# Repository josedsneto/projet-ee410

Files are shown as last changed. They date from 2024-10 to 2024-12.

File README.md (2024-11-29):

# Détecteur de chute

Nous souhaitons développer un capteur de chute, à l'aide d'un axéléromètre 3 Axes.
Lorsqu'une chute est détectée : 
- Une alerte via un vibreur est transmise à l'utilisateur.
- Il dispose de 10 secondes pour confirmer qu'il ne s'est pas évanoui via un bouton.
- Si il a confirmé qu'il était conscient, rien ne se passe.
- En revanche, si il n'a rien confirmé alors une alerte est envoyé par bluetooth sur le téléphone.

## Planning et Deadlines

- 04 Octobre 2024 : Choix du système visé (Remettre une page décrivant le système
imaginé, les mesures qui seront faites + toute autre info pertinente) \
Le [lien](https://docs.google.com/document/d/1k7mpjtoi8ii_IY9sKmL_kZ1YLawBmLwHGLVDXy7D6bw/edit?usp=sharing) vers le document
- 17 Octobre 2024 : Commande de composants 
- 24 Octobre 2024 : Evaluation intermédiaire
- 29 Novembre 2024 : Présentation orale
- 06 Décembre 2023 : Rendu du rapport final écrit 

## Critères pour les profs

L'idée est de faire une première application avec un module compatible Arduino. 
Puis de faire une autre version où on part du composant seul (ou package) et de faire un PCB autour du composant.

A la fin, il faudra comparer les deux.\
Dans notre cas, il s'agit d'un tout ou rien : détection ou non détection. \
Mais nous pouvons récupérer les valeurs des accélérations des 2 capteurs et comparer leurs valeurs.\
De plus nous pouvons réaliser un test statistique sur la détection de chute. (exemple en dessous)

| Cas réel -> | Statique | Chute | Marche |
|-------------|:--------:|:-----:|:------:|
| Statique    |   99%    |  1%   |   0%   |
| Chute       |   1.5%   |  98%  |  0.5%  |
| Marche      |    5%    |  25%  |  70%   |

Et aussi pour la comparaison des 2 capteurs

|                | Capteur1 | Capteur2 |
|----------------|:--------:|:--------:|
| Statique       |   99%    |   99%    |
| Marche         |   97%    |   98%    |
| Chute droite   |   80%    |   98%    |
| Chute en avant |   95%    |   95%    |

Et ainsi comparer nos 2 capteurs.\
Certes nous n'avons que des valeurs tout ou rien mais nous pouvons dire par plusieurs paramètres si un capteur est mieux qu'un autre.

### Réalisation de tests

Il va falloir pouvoir réaliser des tests qui sont reproductibles !\
Il faut pouvoir obtenir le même résultat en faisant une même manip plusieurs fois.

- Test de la chute droite : 
    - Récupération des valeurs lorsqu'un humain chute, pour avoir une idée de modèle.
    - On peut modéliser cette chute avec un ballon qui tombe sur un matelas en mousse par exemple. Ceci permettra une certaine reproductibilité.
- Test de la chute en avant : 
    - Pareil, récupération des valeurs pour un humain
    - Modélisation par exemple par un balai qui tombe en avant.

**Notes sur les chutes :**
- Faire attention à l'orientation du capteur, son positionnement sur le témoin
- Pouvoir reproduire la chute en toutes conditions

# Capteur de chute V1

On utilise le code ```CapteurChuteV1.ino```

Lorsqu'une chute se passe voici ce que nous pouvons mesurer : 

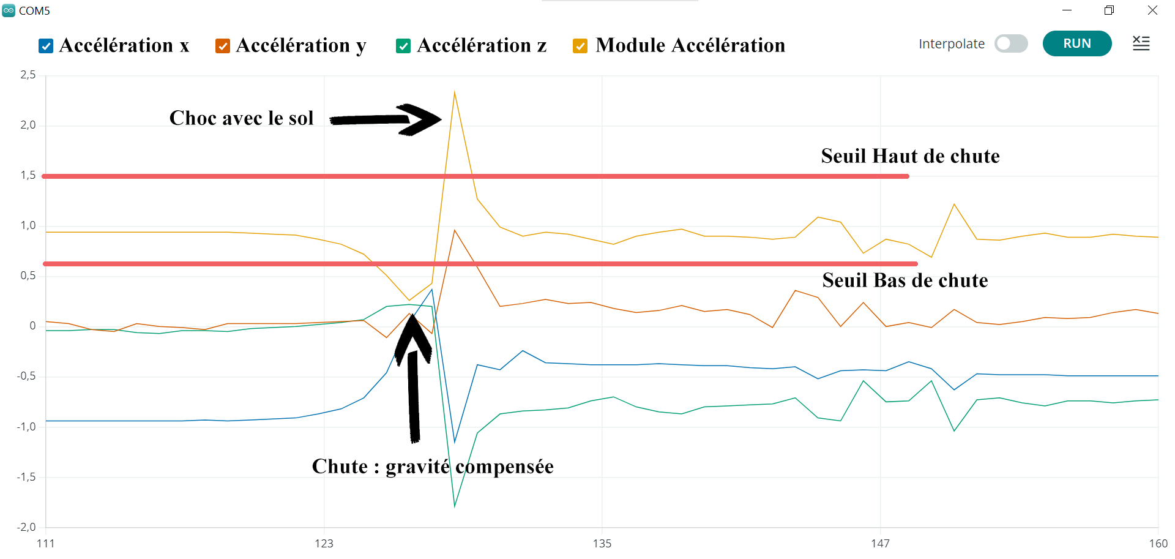
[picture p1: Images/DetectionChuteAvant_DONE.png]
Schéma temporel de la détection de chute


Lorsque le module passe en dessous du seuil bas, c'est le début de la chute : la gravité est compensée par la chute.\
Puis on repasse au dessus du seuil haut, c'est lorsqu'on heurte le sol : gravité + impact avec le sol.

Badé sur ce modèle, nous créons le code arduino ```CapteurChuteV1.ino```, qui utilise un diagramme d'état. \
Voici son schéma : 

Diagramme Etat V1

# Le nouveau capteur

Nous rédigeons un tableau comparatif entre les 2 capteurs : 

|                      |      ADXL 345       |      ADXL 359      |
|----------------------|:-------------------:|:------------------:|
| Interface            |      SPI, I²C       |      SPI, I²C      |
| Technologie utilisée |        MEMS         |        MEMS        |
| Plage de mesure      | ±2g, ±4g, ±8g, ±16g |  ±10g, ±20g, ±40g  |
| Résolution           |       13 bits       |      20 bits       |
| Bruit                |     380 µg/√Hz      |     80 µg/√Hz      |
| 0g Offset            |        ±150 mg      |       ±125 mg      |
| Taille du boîtier    | 3 mm × 5 mm × 1 mm  | 4 mm × 4 mm × 1 mm |

**La technologie MEMS (Micro-Electro-Mechanical Systems).**\
 Un dispositif MEMS est composé de minuscules éléments comme des ressorts, des leviers et des masses mobiles  qui sont gravés sur du silicium.\
 Lorsqu'une force externe (comme une accélération) agit sur ces éléments, cela provoque un mouvement des masses et viens déformer les ressorts. Ce mouvement viens changer la valeur de capacité, ce qui vient influer sur le signal électrique, nous récupérons ainsi des informations sur l'accélération.

Voici le schéma de l'ADXL 359.

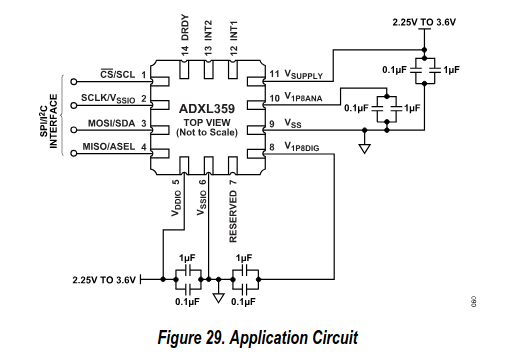
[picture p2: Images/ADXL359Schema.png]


| Pin N° | Mnemonic |                                                                                            Description                                                                                            |
|--------|:--------:|:-------------------------------------------------------------------------------------------------------------------------------------------------------------------------------------------------:|
| 1      |   SCL    |                                                                             Serial Communications Clock for I2C (SCL)                                                                             |
| 2      |  Vssio   |                                                                           Connected to Pin 6 (VSSIO) to enable I2C mode                                                                           |
| 3      |   SDA    |                                                                                    Serial Data for I2C (SDA).                                                                                     |
| 4      |   ASEL   |                                                                           Alternate I2C Address Select for I2C (ASEL).                                                                            |
| 5      |  Vddio   |                                                                                 Digital Interface Supply Voltage                                                                                  |
| 6      |  Vssio   |                                                                                          Digital Ground                                                                                           |
| 7      | RESERVED |                                                                    Reserved. This pin can be connected to ground or left open.                                                                    |
| 8      | V1P8DIG  |                                 Digital Supply. This pin requires a decoupling capacitor. If VSUPPLY connects to VSS, supply the voltage to this pin externally.                                  |
| 9      |   Vss    |                                                                                           Analog Ground                                                                                           |
| 10     | V1P8ANA  |                                  Analog Supply. This pin requires a decoupling capacitor. If VSUPPLY connects to VSS, supply the voltage to this pin externally.                                  |
| 11     | VSUPPLY  | Supply Voltage. When VSUPPLY equals 2.25 V to 3.6 V, VSUPPLY enables the internal LDO regulators to generate V1P8DIG and V1P8ANA. For VSUPPLY = VSS, V1P8DIG and V1P8ANA are externally supplied. |
| 12     |   INT1   |                                                                                          Interrupt Pin 1                                                                                          |
| 13     |   INT2   |                                                                                          Interrupt Pin 2                                                                                          |
| 14     |   DRDY   |                                                                                          Data Ready Pin.                                                                                          |

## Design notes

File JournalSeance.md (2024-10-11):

# Séance 1 : 13 Septembre 2024

Découverte du projet. \
Lecture des attendus.\
Légère prise en main de la boite Arduino.

## Séance 2 : 20 Septembre 2024

Prise en main des capteurs de la boite.\
Tutoriel sur les capteurs suivants : 
- Capteur d'humidité
- Bouton
- Module Bluetooth
- 7 Segement Display

## Séance 3 : 27 Septembre 2024

Création du ```README.md```, définition des tests.\
Echange avec le prof sur le sujet.\
Renseignement sur manière de caractériser notre capteur.\
Prise en main de capteur, communication Bluetooth, test du buzzer avec l'accéléromètre.

## Séance 4 : 4 Octobre 2024

- [X] Exporter des donnés au format csv (du capteur)
- [ ] Chercher capteur équivalent (non Arduino) et se renseigner sur la circuiterie autour
- [ ] Création du fichier de rapport
- [X] Faire le fichier sur l'application Technique

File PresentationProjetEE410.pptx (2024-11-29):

## Capteur de Chute

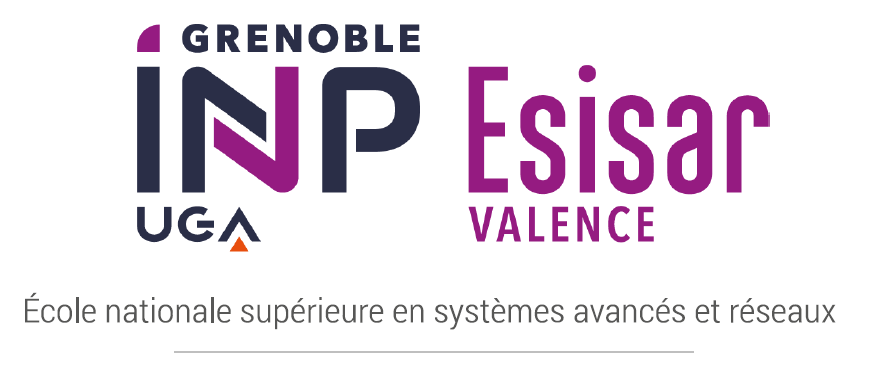
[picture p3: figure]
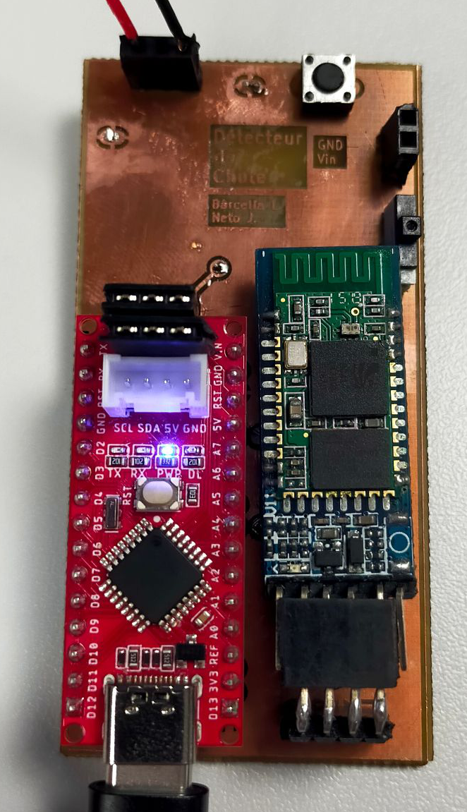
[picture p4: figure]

Projet EE410, Année 2024-2025
Léo BARCELLA & José NETO

## Fonctionnement du capteur (1/2)

Principe général : Fonctionnement simplifié

Technologie MEMS (Micro Systèmes Electromécaniques) :
- Une petite “masse suspendue” bouge sous l’effet de l’accélération
- Capteurs capacitifs mesurent le déplacement
- Mesures transformées en données d’accélération

## Fonctionnement du capteur (2/2)

Illustration du principe

Technologie MEMS (Micro Systèmes Electromécaniques) :

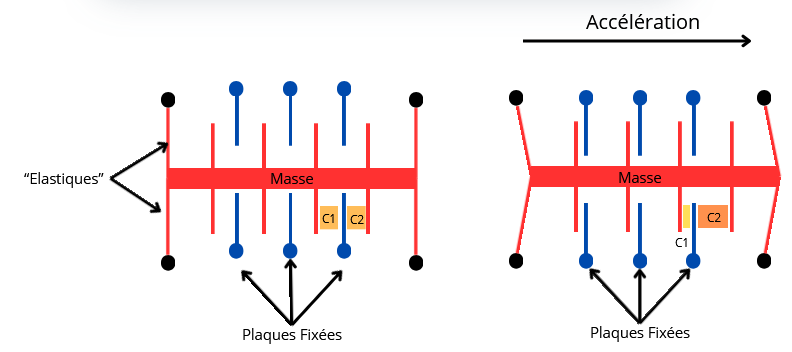
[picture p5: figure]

## Application du capteur (1/3)

Simulation d’un chute

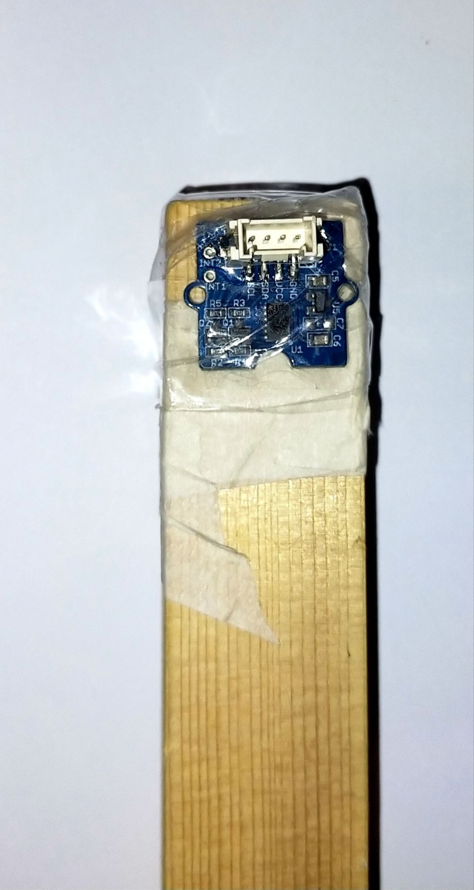
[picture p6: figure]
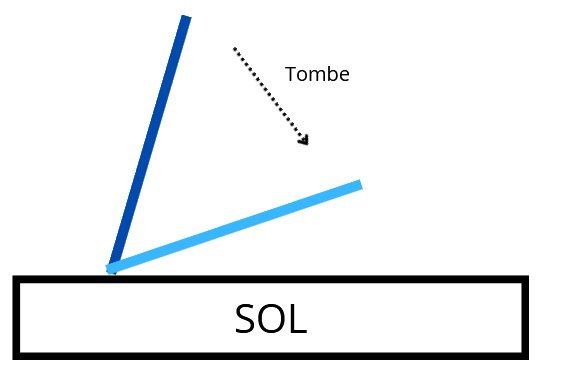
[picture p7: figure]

ADXL345

## Application du capteur (2/3)

Principe général

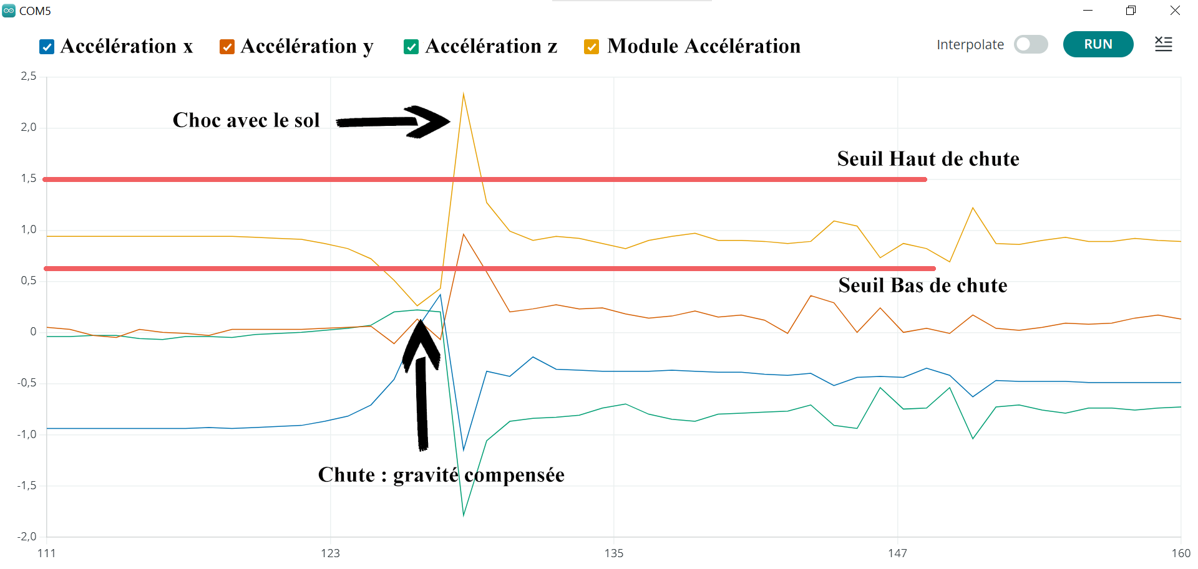
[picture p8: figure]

## Application du capteur (3/3)

Calcul des seuils

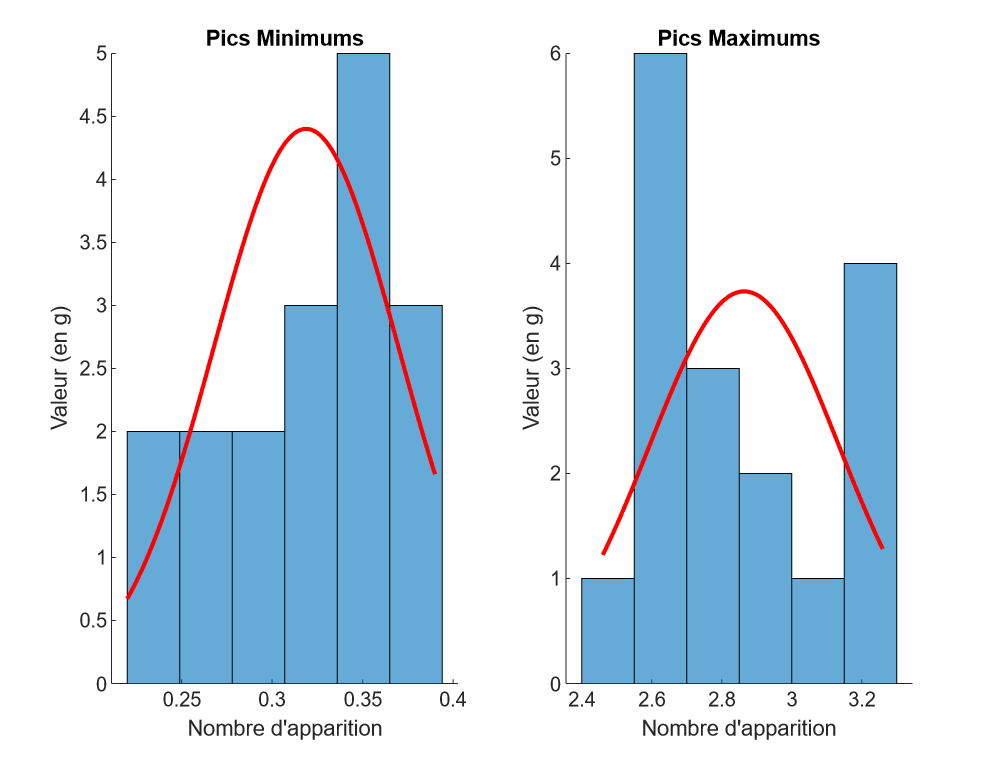
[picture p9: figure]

## Présentation rapide du code

Machine de Mealy

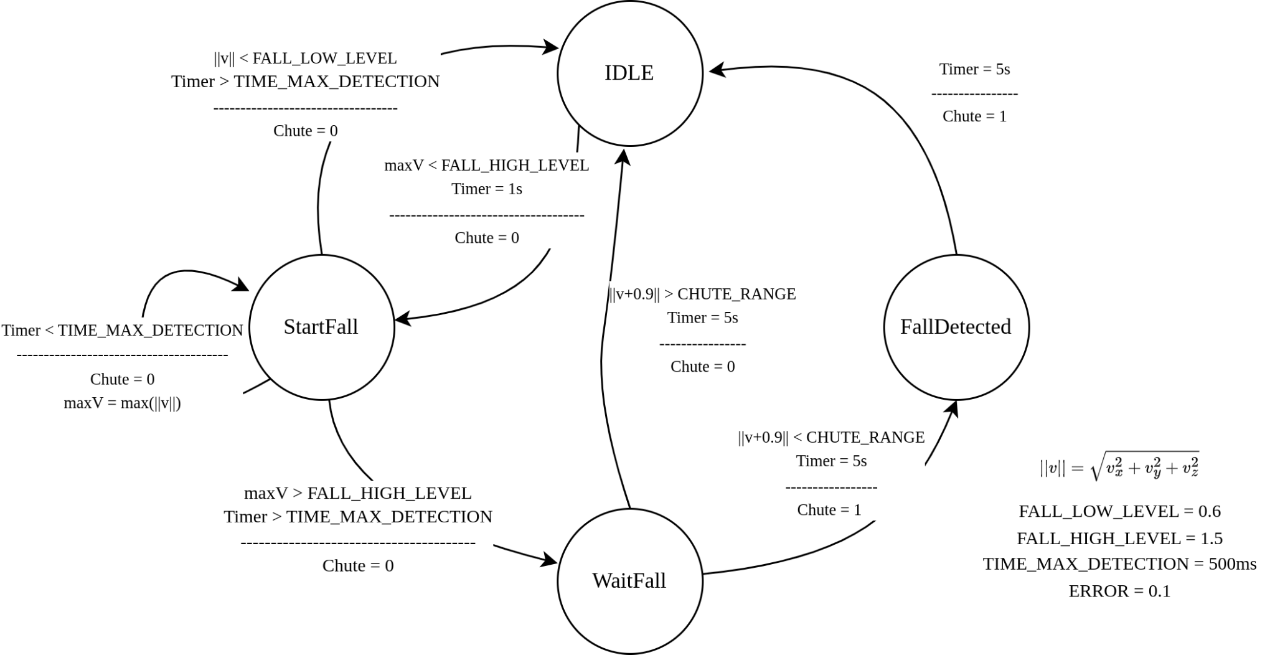
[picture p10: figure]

## Création de la carte (1/4)

Schéma

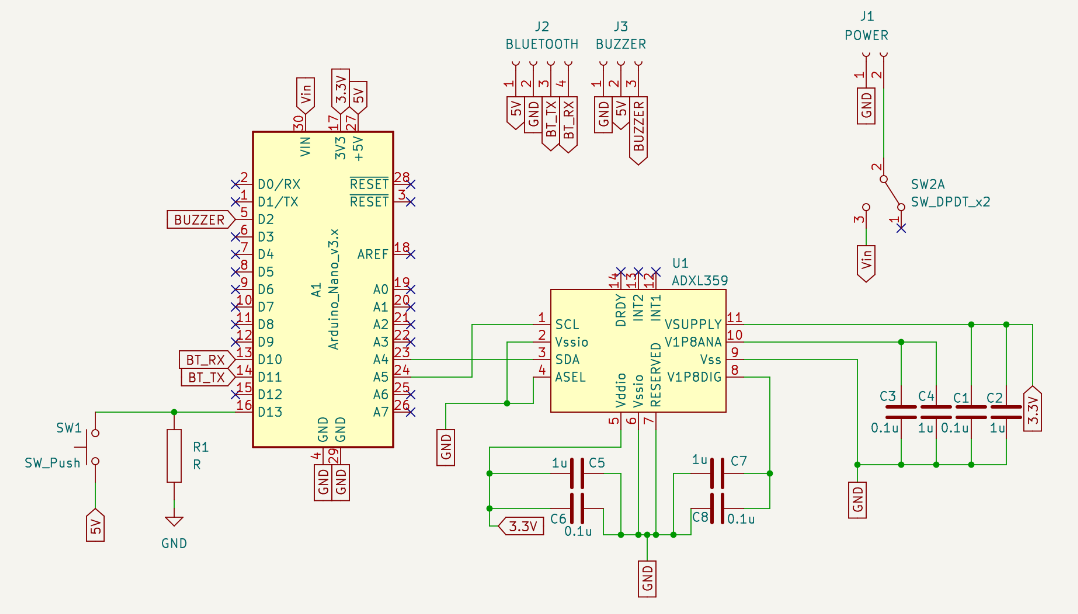
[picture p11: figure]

## Création de la carte (2/4)

Routage

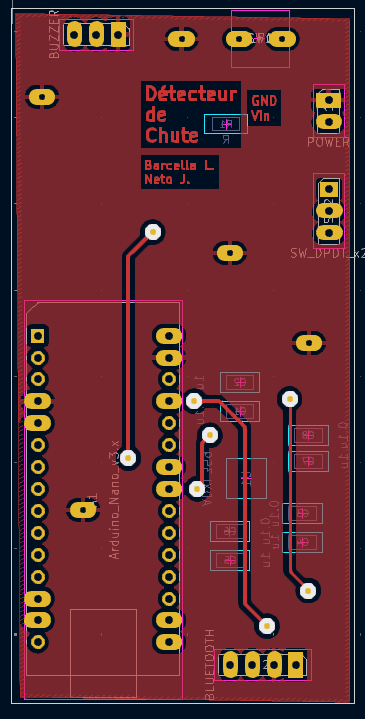
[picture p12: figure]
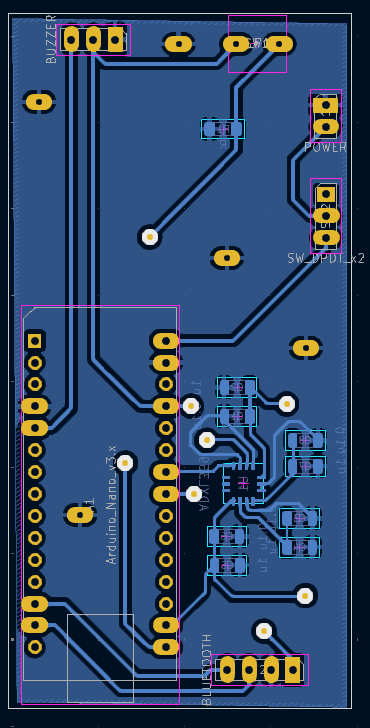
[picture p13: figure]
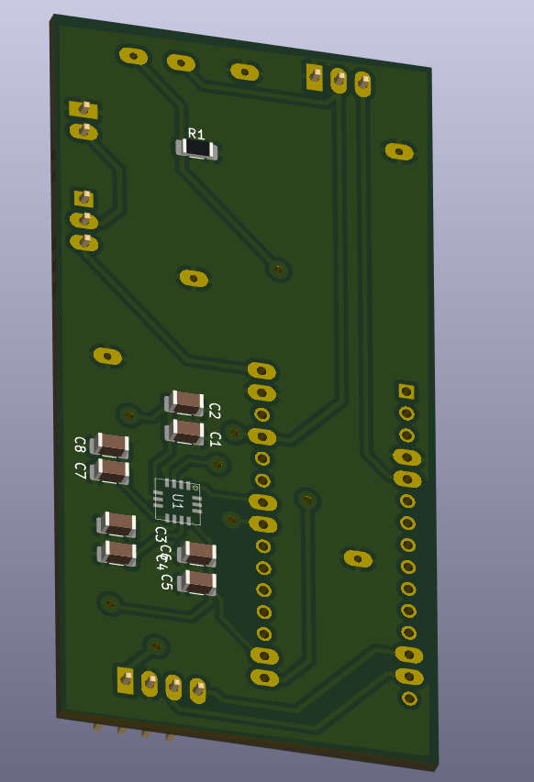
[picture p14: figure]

## Création de la carte (3/4)

Routage : Amélioration de la carte

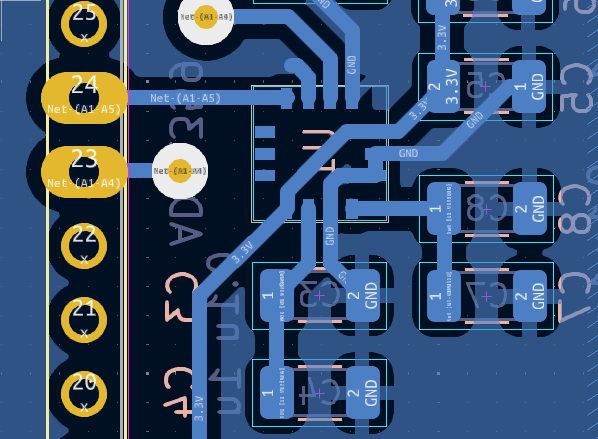
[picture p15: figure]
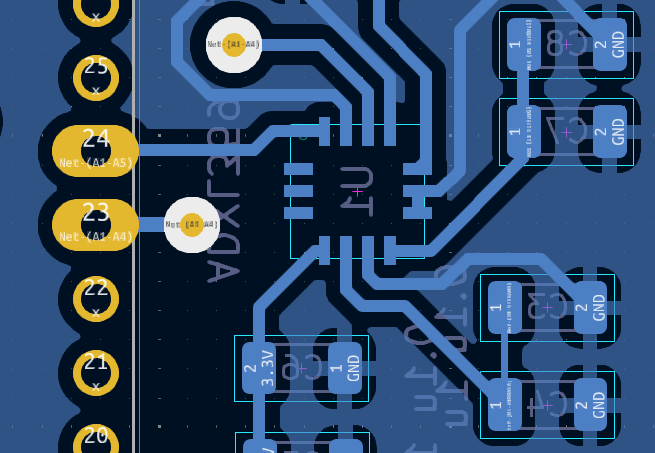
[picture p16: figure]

Version 1

Version 2

## Création de la carte (4/4)

Résultat final

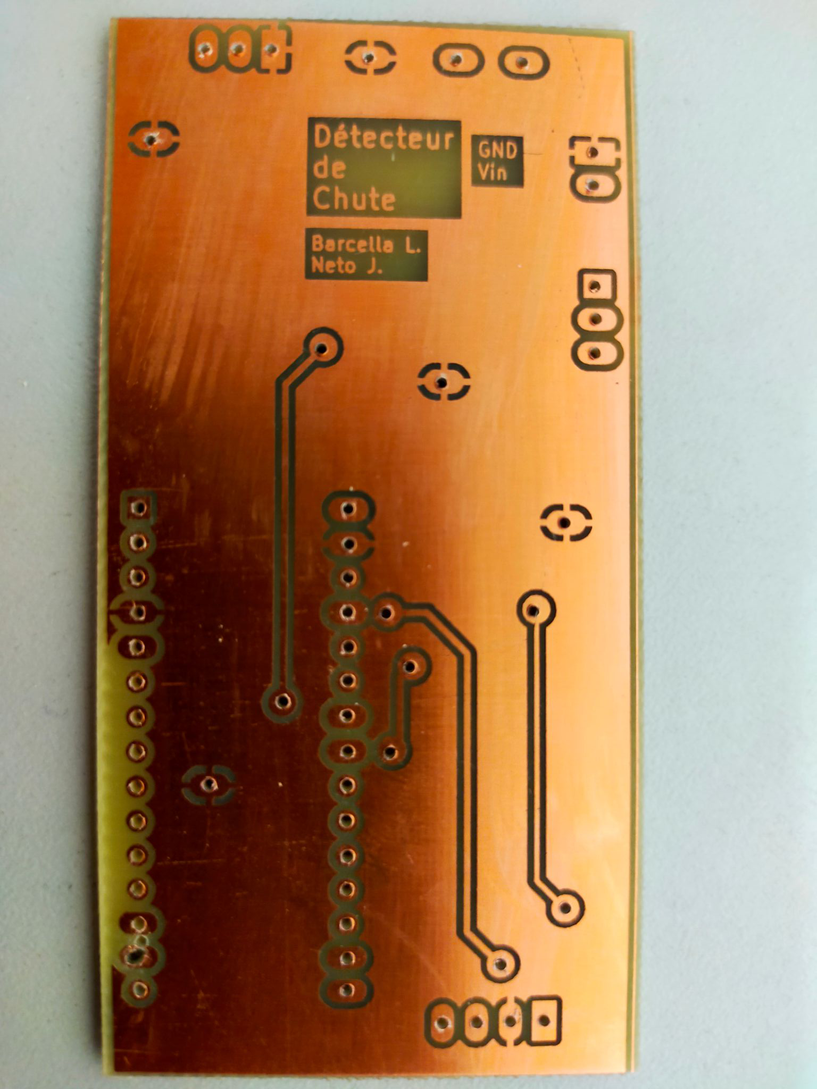
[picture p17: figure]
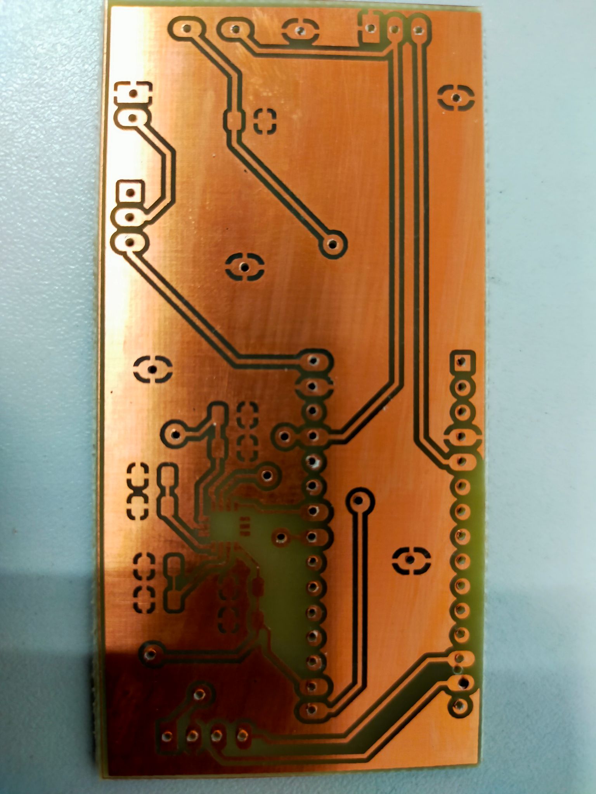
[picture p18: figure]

## Démonstration (1/3)

État initial

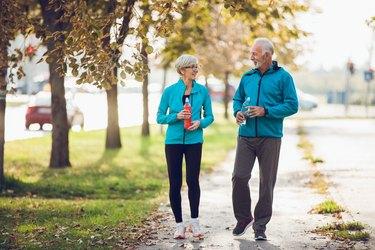
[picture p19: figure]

## Démonstration (2/3)

Est-ce que tout va bien?

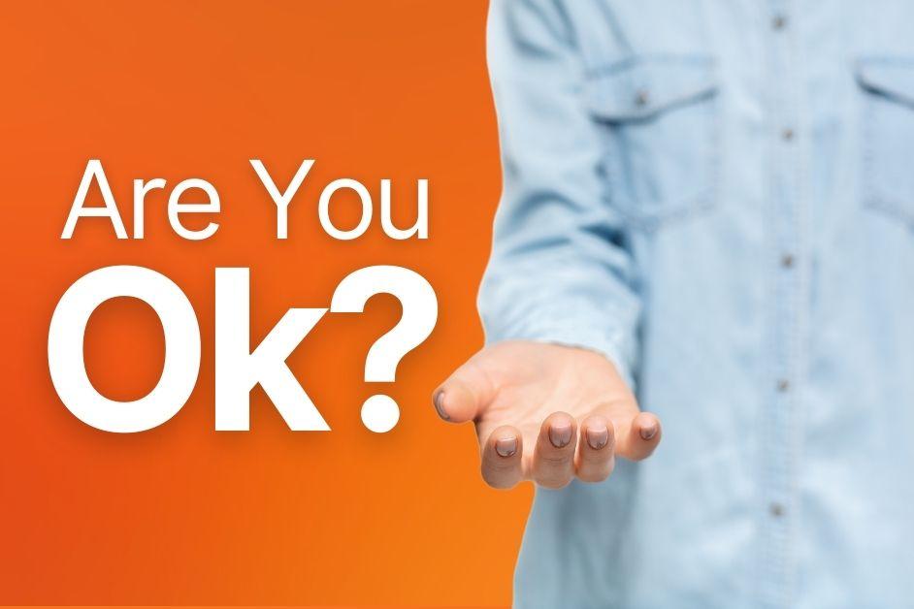
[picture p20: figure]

## Démonstration (3/3)

Finalement, les scénarios possibles

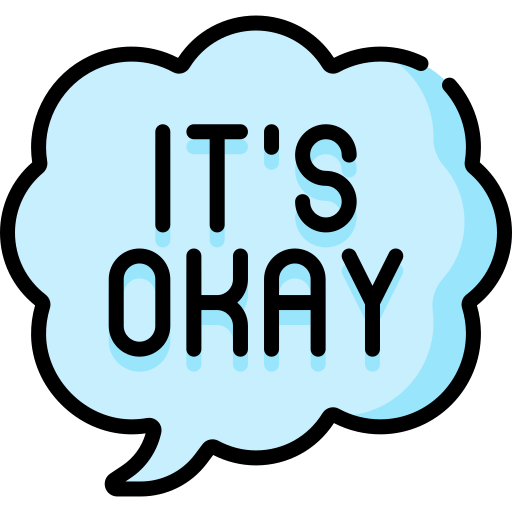
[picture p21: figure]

## Différences entre les 2 capteurs (1/4)

| ADXL 345 (Arduino) | ADXL 359
Interface | SPI, I²C | SPI, I²C
Technologie utilisée | MEMS | MEMS
Plage de mesure | ±2g, ±4g, ±8g, ±16g | ±10g, ±20g, ±40g
Résolution | 13 bits | 20 bits
Bruit | 380 µg/√Hz | 80 µg/√Hz
0g Offset | ±150 mg | ±125 mg
Taille du boîtier | 3 mm × 5 mm × 1 mm | 4 mm × 4 mm × 1 mm

Caractéristiques principales

## Différences entre les 2 capteurs (2/4)

Estimation du 0g Offset et du Gain : Calcul

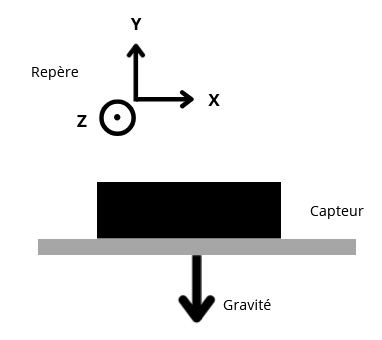
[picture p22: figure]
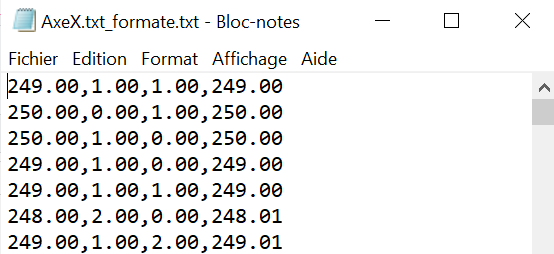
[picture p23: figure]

## Différences entre les 2 capteurs (3/4)

Estimation du 0g Offset et du Gain : Résultats

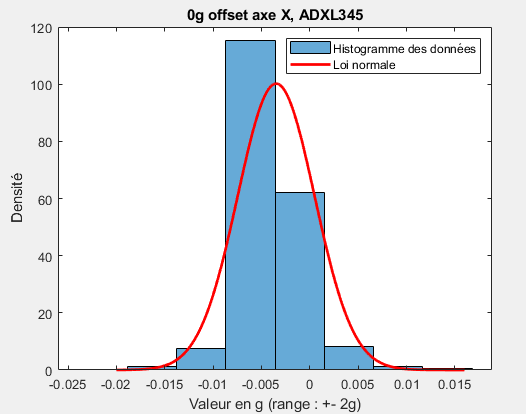
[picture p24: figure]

| ADXL 345 (Arduino) | ADXL 359
0g Offset (expérimental) | 3,5 mg | 7,15 mg
0g Offset (nominal) | ±150 mg | ±125 mg
Gain (expérimental) | 3,9526 mg/LSB (±2g) | 38,93 µg/LSB (±20g)
Gain (nominal) | 3,9 mg/LSB (±2g) | 39 µg/LSB (±20g)

## Différences entre les 2 capteurs (4/4)

Module (de l’accélération) lors d’une chute

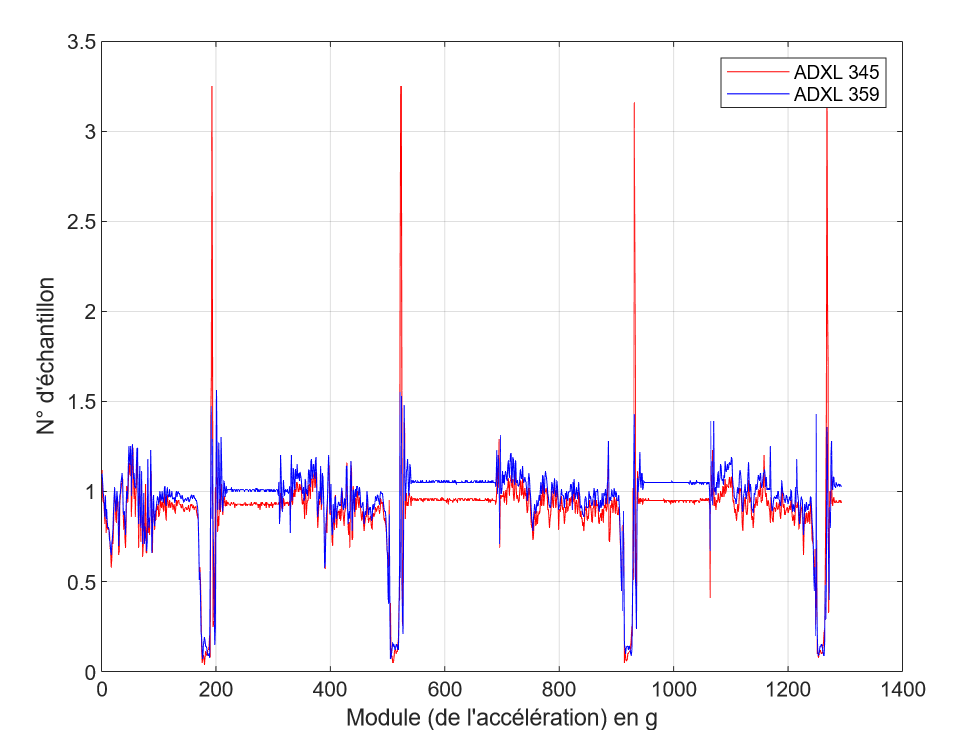
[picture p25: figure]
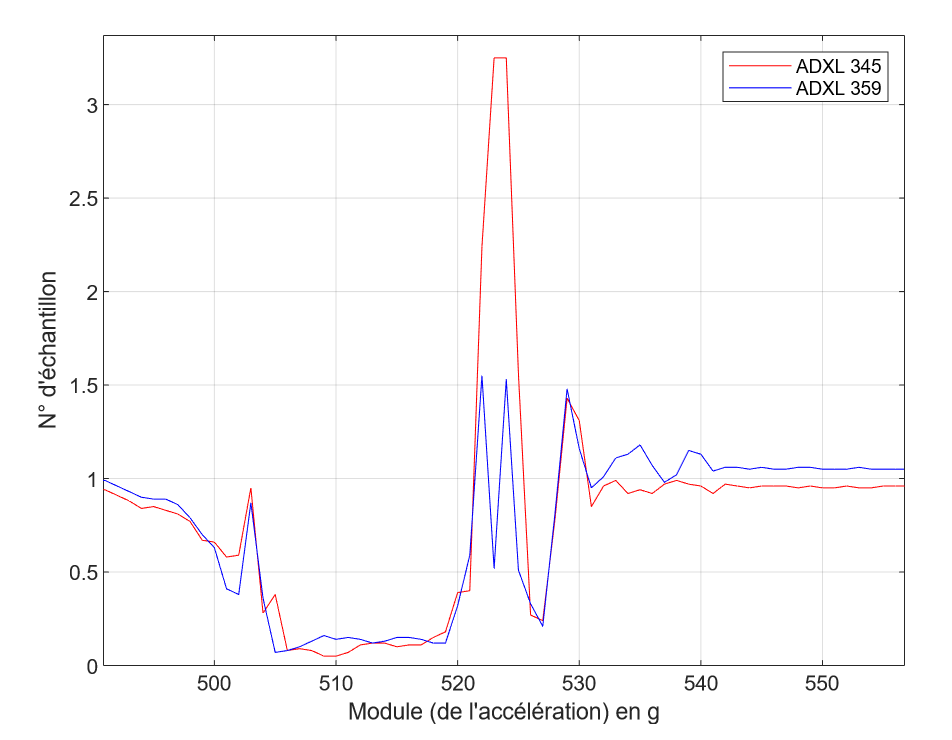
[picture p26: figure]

## Bilan

Bilan général

Ce que nous avons appris :
- Prise en main d’un capteur
- Déchiffrage d’une datasheet
- Réalisation d’un PCB
- Utilisation du matériel pour souder les composants
Ce que nous retenons pour la suite, points d’amélioration :
- 1 semaine pour le PCB n’était pas assez
- Ne pas faire passer de routes sous le capteur !
- Prévoir un planning et répartir les tâches
- Adapter le choix des composants aux moyen disponnibles pour le PCB

## MERCI pour votre attention

Remerciements :
- Claude CANTELLI
- David DREVET
- Dahmane ALLANE

Léo BARCELLA & José NETO

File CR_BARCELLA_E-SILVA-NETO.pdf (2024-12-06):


# Déctecteur de Chute

AUTHORS

BARCELLA Léo - EIS/ESE1
E SILVA NETO José de Deus - EIS/ESE1

2024-12-06

Compte rendu TP - CE410 | Table des figures

## Table des figures

1 | Schéma simplifié de la technologie MEMS | | 2
2 | Les états de Vérification | | 3
3 | Différents scénarios possibles | | 4
4 | Dispositif des premiers tests | | 4
5 | Valeurs de l’accélération lors d’une chute | | 5
6 | Machine de Mealy | | 6
7 | Dessin schématique | | 7
8 | Routage de la carte finale | | 8
9 | Routage du capteur problématique | | 8
10 | Capteur avec le bon routage | | 9
11 | Comparaison du 0g Offset sur l’axe Y | | 9
12 | Comparaison du module de l’accélération lors d’une chute | | 11
13 | Caractérisation du 0g Offset pour l’ADXL345 | | 14
14 | Caractérisation du 0g Offset pour l’ADXL359 | | 14

Page I of 33

Compte rendu TP - CE410 | Liste des tableaux

## Liste des tableaux

1 | Tableau comparatif des 2 capteurs | | 2
2 | Tableau comparatif des valeurs du 0g Offset | | 10
3 | Tableau comparatif des valeurs de gain | | 10

Page II of 33

Compte rendu TP - CE410 | Acronyms

## Acronymes

I2C Inter-integrated circuit. 4, 6

LSB Bit de Poids Faible. 10

MEMS Microsystème Electromecanique. 1

PCB Circuit Imprimé. 1, 7, 12

Page III of 33

Compte rendu TP - CE410 | Acronyms

## Remerciements

Nous souhaitons tout d’abord exprimer notre gratitude envers toutes les personnes qui nous ont aidées à mener à bien ce projet.

En premier lieu, nos sincères remerciements vont à M. Allane, notre professeur encadrant. Vos recommandations pour orienter notre projet et vos conseils dans les moments critiques ont été d’une aide précieuse. Votre disponibilité et votre expertise nous ont guidés avec efficacité, et vos encouragements ont été une source d’inspiration tout au long de ce travail.

Nous souhaitons également remercier M. Cantelli pour son soutien dans la réalisation des deux PCBs. Son expertise dans ce domaine nous a permis d’échanger à plusieurs reprises pour apporter des améliorations aux conceptions initiales. Ses conseils judicieux nous ont aidés à finaliser ce projet avec succès.

Enfin, nous adressons nos remerciements à M. Drevet, qui nous a guidés dans le choix des composants lors du prototypage de la carte. Sa connaissance approfondie des différents éléments disponibles au magasin nous a permis de réaliser ce projet en utilisant un grand nombre d’objets de récupération, contribuant ainsi à une démarche économique et durable.

Nous tenons également à exprimer notre reconnaissance à nos collègues pour leur soutien lors du projet, leurs échanges constructifs et leur compréhension dans les moments cruciaux. Leur collaboration a été essentielle pour atteindre les objectifs fixés.

Ce rapport est le fruit d’un travail collectif et ne serait pas complet sans l’apport de toutes ces contributions. Nous remercions chaleureusement chacun pour leur implication et leur bienveillance.

Page IV of 33

Compte rendu TP - CE410 | Table des matières

## Table des matières

Liste des Figures | I
Liste des Tableaux | II
Acronymes | III
Remerciements | IV
1 Introduction | 1
2 L’accéléromètre | 1
2.1 La technologie MEMS | | 1
2.2 Différences entre l’ADXL345 et l’ADXL359 | | 2
3 L’application du capteur | 3
3.1 Principe | | 3
3.2 Modélisation d’une chute | | 4
3.3 Le code (machine de Mealy) | | 5
3.4 Récuperation des données de l’ADXL359 | | 6
4 Conception du prototype | 7
4.1 Schématique et routage | | 7
4.2 Réalisation du PCB | | 7
4.3 Problématique lors de la conception | | 8
5 Différences expérimentales entre les 2 capteurs | 9
5.1 Estimation du 0g Offset | | 9
5.2 Estimation du gain | | 10
5.3 Différence des capteurs lors d’une chute | | 11
6 Conclusion | 12
References | 13
7 Appendix A - Caractérisation des paramètres des capteurs | 14
8 Appendix B - Code Arduino | 15
9 Appendix C - Code appel des urgences | 28
10 Appendix D - Code Matlab pour la caractérisation des paramètres | 30

Page V of 33

Compte rendu TP - CE410

## 1 Introduction

Ce projet s’inscrit dans le cadre des cours EE410 et EE470 [1], axés sur l’intégration de systèmes et l’instrumentation autour des capteurs. L’objectif de notre projet est de concevoir un système capable de détecter les chutes, en utilisant un accéléromètre compatible Arduino et un autre accéléromètre nécessitant une intégration spécifique. L’idée finale est d’intégrer les deux capteurs et de comparer leurs performances.

Pour y parvenir, nous avons d’abord utilisé une machine de Mealy pour organiser et gérer les interactions entre le capteur Arduino et le système. Nous avons ensuite choisi un capteur non compatible Arduino, que nous devions intégrer.

Pour intégrer ce nouveau capteur, nous avons réalisé deux Circuit Imprimé (PCB)s, une expérience totalement nouvelle pour nous. Ces circuits ont été conçus à l’aide du logiciel KiCad, ce qui nous a permis de développer nos compétences en conception et design électronique.

Cette expérience a été l’occasion d’apprendre de nouvelles techniques en électronique et en programmation, tout en réalisant un projet concret ayant une application pratique significative.

## 2 L’accéléromètre

### 2.1 La technologie MEMS

Les 2 accéléromètres que nous utilisons : l’ADXL345 (Arduino) [2] et ADXL359 [3] (non Arduino) utilisent la même technologie, la technologie Microsystème Electromecanique (MEMS).

La technologie MEMS repose sur l’intégration de structures mécaniques et de circuits électroniques à l’échelle microscopique, principalement à partir de silicium.
Dans le cas d’un capteur MEMS, comme un accéléromètre, le fonctionnement repose sur une petite masse suspendue à l’intérieur du capteur, reliée par des microstructures flexibles.

Lorsqu’une accélération est appliquée, cette masse se déplace légèrement en raison de l’inertie. Ce déplacement est détecté à l’aide de capteurs capacitifs, qui mesurent les variations de distance entre la masse et des électrodes fixes. Ces variations sont ensuite converties en un signal électrique proportionnel à l’accélération appliquée.

Compte rendu TP - CE410 | 2.2 Différences entre l’ADXL345 et l’ADXL359


FIGURE 1 – Schéma simplifié de la technologie MEMS.

### 2.2 Différences entre l’ADXL345 et l’ADXL359

Nous avons consigné les différences données par les datasheets des 2 capteurs dans le Tableau 1.

| ADXL345 (Arduino) | ADXL359 (non Arduino)
Interface Technologie utilisée Plage de mesure Résolution Bruit 0g Offset Taille du boîtier | SPI, I²C MEMS ±2g, ±4g, ±8g, ±16g 13 bits 380µg/p (Hz) ±150 mg 3 mm × 5 mm × 1 mm | SPI, I²C MEMS ±10g, ±20g, ±40g 20 bits 80µg/p (Hz) ±125 mg 4 mm × 4 mm × 1 mm

TABLE 1 – Tableau comparatif des 2 capteurs.

Nous avons choisis l’ADXL359, car il restait dans la même série que le capteur Arduino ; il n’était simplement pas intégré. De plus, nous souhaitions nous baser sur la librairie de l’ADXL345 [4] pour développer le code de l’ADXL359.

Compte rendu TP - CE410

## 3 L’application du capteur

### 3.1 Principe

Le détecteur de chute va fonctionner comme un système communicant auquel l’Arduino envoi des messages à un serveur, ici, c’est un ordinateur qui s’occupe de prendre la décision d’appeler les urgences en cas de chute.

Pour cela, nous avons choisi d’utiliser le protocole Bluetooth pour envoyer l’état actuel. La gestion des messages reçus par le PC sont gérés par le code Python en section 10. Nous avons 3 étapes, la première est évaluée comme normal, la deuxième est la vérification de chute, c’est-à-dire si on a toutes les caractéristiques d’une chute, et finalement un état d’appel des urgences ou un retour à l’état normal. On représente les situations initiales en les affichant sur l’écran du PC. Ce sont les images de la Fig. 2.


(a) IDLE → StartFall. | (b) StartFall → WaitFall.

FIGURE 2 – Les états de Vérification

De façon similaire, on a différents débouchés possibles. Soit la situation est une fausse alerte (pas de vraie chute), soit l’utilisateur est en situation de danger. Les images sont illutrées à la Fig. 3.

Compte rendu TP - CE410 | 3.2 Modélisation d’une chute


(a) WaitFall → IDLE. | (b) WaitFall → FallDetected.

FIGURE 3 – Différents scénarios possibles

### 3.2 Modélisation d’une chute

Afin de générer les premiers résultats et bien comprendre comment sont caractérisées les chutes. On s’est servi d’un bâton auquel on a branché le capteur sur la pointe et fixé avec un scotch. En suite, nous avons coupé un câble Ethernet pour lier les connecteurs Inter-integrated circuit (I2C) au capteur et à l’Arduino. Le matériel utilisé est illustré à la Fig. 4.


(a) Bâton. | (b) Câble du capteur.

FIGURE 4 – Dispositif des premiers tests

Compte rendu TP - CE410 | 3.3 Le code (machine de Mealy)

Pour modéliser une chute, nous avons simplement placé le bâton à la verticale, puis l’avons poussé pour initier sa chute.
Lors d’une chute, le module de la gravité est compensé par l’effet de la chute : le module diminue par rapport à sa valeur statique.
À la fin de la chute, lorsque le capteur heurte le sol, la gravité et l’accélération due à la chute s’additionnent, ce qui crée un pic sur le module de l’accélération. Le graphique à la Fig. 5 montre l’évolution de l’accélération sur les différents axes ainsi que du module de l’accélération lors d’une chute.
Notre code se base sur ce phénomène pour détecter les chutes. Nous définissons donc les seuils HAUT et BAS de manière arbitraire pour la suite de notre code.


FIGURE 5 – Valeurs de l’accélération lors d’une chute.

### 3.3 Le code (machine de Mealy)

Pour bien modéliser notre système, on a choisi utiliser une machine de Mealy pour essayer d’optimiser le code et avoir les moins d’états possibles. Avec cet objectif, on reprend l’explication en 3.1 et on trouve le diagramme de la Fig. 6.

Compte rendu TP - CE410 | 3.4 Récuperation des données de l’ADXL359

IDLE; StartFall; FallDetected; WaitFall; ||a|| < FALL_LOW_LEVEL Timer > TIME_MAX_DETECTION ---------------------------------- Chute = 0; maxA < FALL_HIGH_LEVEL Timer = 1s ------------------------------------ Chute = 0; maxA > FALL_HIGH_LEVEL Timer > TIME_MAX_DETECTION --------------------------------------- Chute = 0; ||a+0.9|| > CHUTE_RANGE Timer = 5s or Button = 1 ---------------- Chute = 0; ||a+0.9|| < CHUTE_RANGE Timer = 5s ----------------- Chute = 1; Timer = 5s ---------------- Chute = 1; Timer < TIME_MAX_DETECTION --------------------------------------- Chute = 0 maxA = max(||a||)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

FIGURE 6 – Machine de Mealy.

A la Fig. 6 on remarque les détails de ce qu’il passe dans le code Arduino. D’abord si jamais on détecte une accélération au-dessus de 0.6, dans ce cas, l’hypothèse, c’est qu’on a eu une variation contraire à la gravité, donc on espère une valeur plus petite que 1 (la valeur standard étalonné). En suite, on enregistre l’accélération maximale pendant 500 ms. Pendant ce temps-là, pour qu’une chute arrive, il faut que l’utilisateur tombe au sol pour qu’on puisse avoir une valeur d’accélération ajoutée à la gravité : plus grande que 1. Si ça n’arrive pas, on retourne à l’état initial.

Au contraire, si on retrouve les caractéristiques d’une chute, on passe à l’état de vérification, Fig. 2b, dans lequel on attend une réponse du côté utilisateur. En ce cas, le button de non-chute sert à dire que tout se passe bien, sinon une attente plus grande que 5 secondes fait passer le système passer à l’état de danger, et les urgences sont notifiés. De plus, l’utilisateur est notifié par le signal sonore par un buzzer pour représenter l’état de danger [5].

### 3.4 Récuperation des données de l’ADXL359

Pour récupérer les données de l’ADXL, nous utilisons le protocole I2C. Nous avons basé notre code sur la librairie de l’ADXL345 pour nous familiariser avec le fonctionnement du capteur, ainsi que l’utilisation des différentes fonctions.

Dans le cas de l’ADXL359, il n’est pas nécessaire de passer par plusieurs états différents pour l’utiliser. On doit seulement être en mode standby pour changer ses paramètres.

- Mettre le bit 0 de POWER_CTL à 0 : Mode standby
- Régler d’autres paramètres au besoin...
- Mettre le bit 0 de POWER_CTL à 1 : Mode mesure

Compte rendu TP - CE410

- Mesure, en lisant XDATA, YDATA e ZDATA

## 4 Conception du prototype

### 4.1 Schématique et routage

La Fig. 7 présente le schéma utilisé pour l’élaboration du prototype.


FIGURE 7 – Dessin schématique.

### 4.2 Réalisation du PCB

Le PCB et le dessin d’empreinte, sont présentés à la Fig. 8.

Le routage a été fait sur deux couches (ce qui est proposé à l’esisar avec une finesse de gravure minimum de 0.3 mm.

Nous avons choisi de grossir la taille de pads utilisés pour faciliter la soudure, recommandé par
M. CANTELLI. Pour ce qui est des capacités et des résistances nous avons choisi le type 1206, la taille la plus grosse disponnible au magasin de composants de l’école. Dans l’optique ausi de faciliter les soudures.

Pour la soudure de l’ADXL359, nous avons eu recours au four à réfusion : la structure du capteur avec des pads, petits (0.35 mm de large) et sous le capteur ; rendait la soudure impossible au fer à souder. Nous avons donc pu voir son foctionnement (crème à braser, courbe de température à respecter...).

Compte rendu TP - CE410 | 4.3 Problématique lors de la conception


(a) Couche Top. | (b) Couche Bottom.

FIGURE 8 – Routage de la carte finale.

### 4.3 Problématique lors de la conception

La Fig. 9 zoome sur le routage autour du capteur.


FIGURE 9 – Routage du capteur problématique.

Malheureusement, après avoir soudé tous les composants, le capteur ne fonctionnait pas : il ne répondait pas lorsque nous essayions de lire ses données. Après inspection, tous les signaux (SDA, SCL pour l’I²C, 3.3 V et GND) arrivaient correctement jusqu’au bout des pistes, et aucun court-circuit ne perturbait notre carte.
Après avoir demandé conseil à M. CANTELLI et M. ALLANE, nous avons décidé de refaire le routage de la carte autour du capteur (Fig. 10). Nous avons veillé à ce qu’aucune piste ne passe sous le capteur et avons également allongé la taille des pads, de sorte que lorsqu’il y a trop de crème à braser sur les pads, celle-ci se répartisse sur leur longueur, améliorant ainsi la qualité de notre soudure.

Compte rendu TP - CE410


FIGURE 10 – Capteur avec le bon routage.

Après avoir réalisé notre deuxième PCB, le capteur nous renvoyait enfin les résultats liés à l’accélération. Les modifications que nous avons approtés nous a donc permis de réduire l’aléa lié produit par le four à réfusion.

## 5 Différences expérimentales entre les 2 capteurs

### 5.1 Estimation du 0g Offset

Nous essayons de caractériser le 0g Offset du capteur, c’est a dire la valeur qu’il lit lorsqu’il est censé voir 0g sur cet axe. Pour cela, on le place de sorte à ce que la gravité n’agisse que sur un seul axe, celui-ci voit 1g, tandis que les autres axes ne voient que 0g. On répète ensuite l’expérience sur les 2 autres axes pour obtenir 3 lots de données. On peut voir ces résultats à la Fig. 13 pour l’ADXL345 et à la Fig. 14.


(a) ADXL345. | (b) ADXL359.

FIGURE 11 – Comparaison du 0g Offset sur l’axe Y.

Compte rendu TP - CE410 | 5.2 Estimation du gain

On peut voir sur la Figure 11 que le 0g offset suit bien un loi normale centrée en 0. Sur le Tableau 2, on peut voir que nos résultats sont bien dans les critères données pas la datasheet.

| ADXL345 (Arduino, ±2g) | ADXL359 (non Arduino ±20g)
Moyenne 0g offset X expérimental Moyenne 0g offset Y expérimental Moyenne 0f offset Z expérimental 0g offset (range) 0f offset datasheet | 3.39 mg 3.30 mg 3.45 mg ±20 mg ±150 mg | 6.45 mg 2.69 mg -12.3 mg ±40 mg ±125 mg

TABLE 2 – Tableau comparatif des valeurs du 0g Offset.

### 5.2 Estimation du gain

Pour estimer le gain : la valeur que nous devons multiplier à la valeur donnée par le capteur, cette donnée est en g/Bit de Poids Faible (LSB). Nous réutilisons les données que nous avions récupérées pour estimer le 0g Offset.

La formule que nous utilisions est la suivante :
q
(GX × (Xraw − Xof fset))² + (GY × (Yraw − Yof fset))² + (GZ × (Zraw − Zof fset))² = 1. (1)

Cette équation s’applique sur les 3 lots de données que nous avions. Nous avons donc 3 équations (avec différents paramètres) et 3 inconnues (GX, GY et GZ). Les résultats sont résumés dans le Tableau 3.

| ADXL345 (Arduino, ±2g) | ADXL359 (non Arduino ±20g)
Gain axe X expérimental Gain axe Y expérimental Gain axe Z expérimental Gain datasheet | 4.00 mg/LSB 3.99 mg/LSB 3.87 mg/LSB 3.90 mg/LSB | 39.7 µg/LSB 36.3µg/LSB 40.8 µg/LSB 39.0 µg/LSB

TABLE 3 – Tableau comparatif des valeurs de gain.

Compte rendu TP - CE410 | 5.3 Différence des capteurs lors d’une chute

### 5.3 Différence des capteurs lors d’une chute

Nos réalisons une chute aucours de laquelle nous venons mesurer le module de l’accélération sur les deux capteurs (cf : Fig. 12). On peut voir que les capteurs se suivent lorsqu’il y a des variation. Cependant, lorsque l’accélération dépasse 1.5 g, la valeur devient faussée pour l’ADXL359.

Nous avons quelques idée sur les causes de cette erreur :

- Problème de rafraîchissement des valeurs : le code utilisé possède un temps de rafraîchissement de 10 ms du code Arduino, ce qui nous empêche peut-être de récupérer les bonnes valeurs
- Effet de "clipping" : lorsque l’accélération atteint un certain seuil, il est possible que les réponses soit faussées
- Problème d’électronique (le plus probable) : il se peut qu’il y ait un faux contact lorsque le capteur chute sur le sol ce qui vient fausser les résultats.


FIGURE 12 – Comparaison du module de l’accélération lors d’une chute.

Compte rendu TP - CE410

## 6 Conclusion

Ce projet nous a permis de combiner théorie et pratique en concevant un système de détection de chutes basé sur l’intégration de deux capteurs : un compatible Arduino et un autre nécessitant une intégration spécifique. L’utilisation d’une machine de Mealy pour organiser les interactions entre les capteurs et le système a renforcé notre compréhension des machines à états.

Une des grandes leçons tirées de ce projet est l’importance de la sélection des composants en fonction des moyens disponibles. En effet, les contraintes matérielles rencontrées nous ont appris à adapter nos choix et à tirer parti des ressources limitées.

La réalisation des deux PCBs, conçus avec le logiciel KiCad, a été un véritable défi. N’ayant aucune expérience préalable dans ce domaine, nous avons beaucoup appris, que ce soit sur le processus de conception ou sur les étapes nécessaires à leur fabrication et leur utilisation.

En résumé, ce projet nous a permis de développer des compétences variées en électronique et en programmation tout en répondant à une problématique concrète et pratique. Cette expérience, riche en apprentissages, restera un point marquant dans notre parcours académique. [3].

Compte rendu TP - CE410 | Références

## Références

[1] B. V., “III Synthèse RTL.” https://chamilo.grenoble-inp.fr/courses/ESISAR4AMCE419/document/CM/CE410_CE419_III_Synthese_RTL_1_2.pdf?cidReq=ESISAR4AMCE419&id_session=0&gidReq=0&gradebook=0&origin=, (https://chamilo.grenoble-inp.fr/courses/ESISAR4AMCE419/document/CM/CE410_CE419_III_Synthese_RTL_1_2.pdf?cidReq=ESISAR4AMCE419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) 2024. Accessed : 06-12-2024.
[2] Analog Devices, 3-Axis, ±2 g/±4 g/±8 g/±16 g Digital Accelerometer, 05 2022. Rev. G.
[3] Analog Devices, Low Noise, Low Drift, Low Power 3-Axis MEMS Accelerometer, 06 2023. Rev. 0.
[4] Speed-Studio, | “Accelerometer_ADXL345.” | https://github.com/Seeed-Studio/
Accelerometer_ADXL345, (https://github.com/Seeed-Studio/Accelerometer_ADXL345) 2024.
[5] B. A. Nassim, “Star-Wars-theme-Song-Arduino-.” https://github.com/NassimBouyacoub/Star-Wars-theme-Song-Arduino-/tree/master, (https://github.com/NassimBouyacoub/Star-Wars-theme-Song-Arduino-/tree/master) 2013.

Compte rendu TP - CE410

## 7 Appendix A - Caractérisation des paramètres des capteurs


(a) Axe X | (b) Axe Y | (c) Axe Z

FIGURE 13 – Caractérisation du 0g Offset pour l’ADXL345


(a) Axe X | (b) Axe Y | (c) Axe Z

FIGURE 14 – Caractérisation du 0g Offset pour l’ADXL359

Compte rendu TP - CE410

## 8 Appendix B - Code Arduino

//IMPERIAL MARCH
const int c = 261;
const int d = 294;
const int e = 329;
const int f = 349;
const int g = 391;
const int gS = 415;
const int a = 440;
const int aS = 455;
const int b = 466;
const int cH = 523;
const int cSH = 554;
const int dH = 587;
const int dSH = 622;
const int eH = 659;
const int fH = 698;
const int fSH = 740;
const int gH = 784;
const int gSH = 830;
const int aH = 880;

const int buzzerPin = 2; // Digital Pin 8
const int ledPin1 = 12; | // Digital Pin 12
const int ledPin2 = 13; | // Digital Pin 13 Built In Led can Change it if you want

int counter = 0;

//#include <Wire.h>
#include <ADXL345.h>

#include <SoftwareSerial.h>

#define BUTTON_PIN 13

#define BUZZER 2

#define FALL_LOW_LEVEL 0.6

#define FALL_HIGH_LEVEL 1.5

// Time during which we look to see if there has been a peak in acceleration (in milliseconds)

Compte rendu TP - CE410

#define TIME_FALL_MAX_DETECTION 500

#define CHUTE_ERROR 0.4 //Margin d'erreur sur laquel une personne peut buger sans que le système comprendre comme //false chute

#include <Wire.h>

//double xyz[3];
//// Les valeurs de l'accélération suivant les différents axes //double ax, ay, az;
//double ;
double maxModuleValue = 1;
int buttonValue;
bool chuteLabel = false; //when in waiting state, this label is resposible for passing to the FallDetected.

double xyz359[3];
// Les valeurs de l'accélération suivant les différents axes double ax359, ay359, az359;
double module359;

// =========================Valeurs pour la librairie =========================

byte _buff359[9] ; | //6 bytes buffer for saving data read from the device
double gains359[3]; | // counts to Gs
bool status359; | // set when error occurs
// see error code for details
byte error_code359; | // Initial state
#define ADXL359_DEVICE (0x1D) | // ADXL359 device address for I2C

#define ADXL359_TO_READ (9) | // num of bytes we are going to read each time (two bytes for each axis)

#define ADXL359_OK | 1 // no error

#define ADXL359_ERROR 0 // indicates error is present

#define ADXL359_NO_ERROR 0 // initial state #define ADXL359_READ_ERROR 1 // problem reading accel #define ADXL359_BAD_ARG 2 // bad method argument

#define ADXL359_STATUS 0x04

Compte rendu TP - CE410

#define ADXL359_THRESH_ACT_H 0x25 // Registre du theresold activation

#define ADXL359_THRESH_ACT_L 0x26 // Registre du theresold activation

#define ADXL359_ACT_COUNT 0x27 // Number of consecutive events above threshold (from ACT_THRESH) required to detect activity #define ADXL359_DATAX3 0x08

#define ADXL359_POWER_CTL 0x2d

#define ADXL359_RANGE 0x2C // Setting the range

#define ADXL359_FILTER 0x28 // Filter settings #define ADXL359_OFFSET_X_H 0x1E

SoftwareSerial mySerial(11, 10); // RX, TX

// Enumeration of the differents states enum State {
Idle,
StartFall,
WaitFall,
FallDetected
};

// The current State
State CS = Idle;

long startTime;
long startWaitTime;
long startFallTime;
long startOkTime;

void setup() {
mySerial.begin(9600);
mySerial.println("Starting Bluetooth Connection");

pinMode(BUTTON_PIN, INPUT);
pinMode(BUZZER, OUTPUT);

//digitalWrite(BUZZER, LOW);

// put your setup code here, to run once: Serial.begin(9600);
//for 20g

Compte rendu TP - CE410

gains359[0] = 0.000039; gains359[1] = 0.000039; gains359[2] = 0.000039;
// for 10g
// gains359[0] = 0.0000195; | gains359[1] = 0.0000195; | gains359[2] = 0.0000195;

// Start communication
Wire.begin();

//Turning on the ADXL359
setRegisterBit359(ADXL359_POWER_CTL, 0, 1); // Go to Standby Mode, must go to measurment mode after setup. delay(100);

// Set range to +- 20g
setRegisterBit359(ADXL359_RANGE, 0, 0); setRegisterBit359(ADXL359_RANGE, 1, 1);

setRegisterBit359(ADXL359_POWER_CTL, 0, 0); // Go to measurment mode

}

void loop() {
getAcceleration359(xyz359);
getAccelerometerValues359();
module359 = sqrt(ax359 * ax359 + ay359 * ay359 + az359 * az359); // We calculate de magnitude buttonValue = digitalRead(BUTTON_PIN);

// The running of the fallDetector => Following an ASM
runASM();

// printAccelerationAndModule359();
delay(200);

}

void writeTo359 (byte address, byte val) { Wire.beginTransmission(ADXL359_DEVICE); // start transmission to device
Wire.write(address); | // send register address
Wire.write(val); | // send value to write
Wire.endTransmission(); | // end transmission
}

Compte rendu TP - CE410

bool getRegisterBit359(byte regAdress, int bitPos) { byte _b;
readFrom359(regAdress, 1, &_b);
return ((_b >> bitPos) & 1);
}

void setRegisterBit359(byte regAdress, int bitPos, bool state) { byte _b;
readFrom359(regAdress, 1, &_b);
if (state) {
_b |= (1 << bitPos); | // forces nth bit of _b to be 1. | all other bits left alone.
} else {
_b &= ~(1 << bitPos); // forces nth bit of _b to be 0. all other bits left alone. }
writeTo359(regAdress, _b);
}

void getAcceleration359(double* xyz) { int i;
int xyz_int[3];
readAccel359(xyz_int);
for (i = 0; i < 3; i++) {
xyz359[i] = xyz_int[i] * gains359[i]; }
}

// Reads the acceleration into three variable x, y and z void readAccel359(int* xyz) {
readXYZ359(xyz, xyz + 1, xyz + 2);
}
void readXYZ359(int* x, int* y, int* z) {
uint8_t buffer[9]; // Buffer pour lire 3 axes (3 octets par axe) readFrom359(ADXL359_DATAX3, 9, buffer); // Lire 9 octets à partir du registre DATAX0

// Extraction des données brutes sur 20 bits pour chaque axe
*x = (int)((((uint32_t)(buffer[0])) << 12) |
(((uint32_t)(buffer[1])) << 4) | (((uint32_t)(buffer[2])) >> 4));

Compte rendu TP - CE410

*y = (int)((((uint32_t)(buffer[3])) << 12) | (((uint32_t)(buffer[4])) << 4) |
(((uint32_t)(buffer[5])) >> 4));

*z = (int)((((uint32_t)(buffer[6])) << 12) | (((uint32_t)(buffer[7])) << 4) |
(((uint32_t)(buffer[8])) >> 4));

// Sign extension pour convertir les valeurs 20 bits en entiers signés if (*x & 0x80000) *x |= 0xFFF00000; // Si bit 20 = 1, étendre le signe if (*y & 0x80000) *y |= 0xFFF00000; // Idem pour Y
if (*z & 0x80000) *z |= 0xFFF00000; // Idem pour Z
}

// Reads num bytes starting from address register on device in to _buff array void readFrom359(byte address, int num, byte _buff[]) { Wire.beginTransmission(ADXL359_DEVICE); // start transmission to device
Wire.write(address); | // sends address to read from
Wire.endTransmission(false); | // end transmission

Wire.beginTransmission(ADXL359_DEVICE); // start transmission to device Wire.requestFrom(ADXL359_DEVICE, num); // request 6 bytes from device

int i = 0;
while (Wire.available()) { | // device may send less than requested (abnormal)
_buff[i] = Wire.read(); | // receive a byte
i++;
}
if (i != num) {
status359 = ADXL359_ERROR;
error_code359 = ADXL359_READ_ERROR;
}
Wire.endTransmission(); | // end transmission
}

void getAccelerometerValues359() { getAcceleration359(xyz359);

Compte rendu TP - CE410

ax359 = xyz359[0]; ay359 = xyz359[1]; az359 = xyz359[2]; }

void printAccelerationAndModule359() { Serial.print(ax359);
Serial.print(",");
Serial.print(ay359);
Serial.print(",");
Serial.print(az359);
Serial.print(",");
Serial.println(module359); }

void runASM() {
// Notre diagramme d'Etat
switch (CS) {
case Idle:
// Current working
//digitalWrite(BUZZER, LOW); Serial.print(module359);
Serial.println(",idle");
mySerial.println("idle");

if (module359 < FALL_LOW_LEVEL) { // Maybe there is a fall CS = StartFall;
//maxModuleValue = 1; // Valeur neutre
//startTime = millis(); // Start Measuring time
}

break;

case StartFall:
startTime = millis();

while ((millis() - startTime) < TIME_FALL_MAX_DETECTION) { // Si on a dépassé le temps d'enregistrement des valeurs getAccelerometerValues359();
module359 = sqrt(ax359 * ax359 + ay359 * ay359 + az359 * az359);
maxModuleValue = max(maxModuleValue, module359);

if (module359 > FALL_HIGH_LEVEL) {

Compte rendu TP - CE410

Serial.print(module359);
Serial.println(",analyse"); delay(100);
}
}

if (maxModuleValue > FALL_HIGH_LEVEL) { // Il y a bien eu une chute CS = WaitFall;
}
else {
CS = Idle;
//Serial.print("Pas de chute détectée finalent, max Module : "); //Serial.println(maxModuleValue);
Serial.print(module359);
Serial.print(",ok");
mySerial.println("ok");
}

break;

case WaitFall:
startWaitTime = millis();

while ((millis() - startWaitTime) < 5000) { // On attend 5 seconds pour voir si la personne va bien getAccelerometerValues359();
buttonValue = digitalRead(BUTTON_PIN);

module359 = sqrt(ax359 * ax359 + ay359 * ay359 + az359 * az359);
//Serial.println(module);

if ((0.9 - CHUTE_ERROR < module359) and (module359 < 0.9 + CHUTE_ERROR) and (digitalRead(BUTTON_PIN) == false)){ CS = WaitFall;
Serial.print(module359);
Serial.println(",waiting");
mySerial.println("waiting"); //digitalWrite(BUZZER, HIGH); delay(100);
chuteLabel = true;

} else {

Compte rendu TP - CE410

startOkTime = millis();
CS = Idle;
chuteLabel = false;

while ((millis() - startOkTime) < 5000) { //digitalWrite(BUZZER, LOW); Serial.print(module359);
Serial.println(",ok");
mySerial.println("ok");
delay(100);
}

break;
}
}

if (chuteLabel == true) {
CS = FallDetected;
} else {
CS = Idle;
}
break;

case FallDetected:
//digitalWrite(BUZZER, LOW); startFallTime = millis();
CS = Idle;

while ((millis() - startFallTime) < 10) { Serial.print(module359);
Serial.println(",danger"); mySerial.println("danger"); IMPERIALMARCH();
delay(100);
}

//Serial.print("Chute détectée !!!!!!!!!!!!!!!!!!!!!! max :"); //Serial.println(maxModuleValue);
//delay(5000);

Compte rendu TP - CE410

//Serial.println("Retour etat initial");

break;

default :
Serial.println("Not a State, Error"); delay(1000);
break;
}
}

void beep(int note, int duration) {
//Play tone on buzzerPin
tone(buzzerPin, note, duration);

//Play different LED depending on value of 'counter' if(counter % 2 == 0)
{
digitalWrite(ledPin1, HIGH);
delay(duration);
digitalWrite(ledPin1, LOW); }else
{
digitalWrite(ledPin2, HIGH); delay(duration);
digitalWrite(ledPin2, LOW); }

//Stop tone on buzzerPin
noTone(buzzerPin);

delay(50);

//Increment counter
counter++;
}

void firstSection()
{

Compte rendu TP - CE410

beep(a, 500);
beep(a, 500);
beep(a, 500);
beep(f, 350);
beep(cH, 150);
beep(a, 500);
beep(f, 350);
beep(cH, 150);
beep(a, 650);

delay(500);

beep(eH, 500);
beep(eH, 500);
beep(eH, 500);
beep(fH, 350);
beep(cH, 150);
beep(gS, 500);
beep(f, 350);
beep(cH, 150);
beep(a, 650);

delay(500);
}

void secondSection()
{
beep(aH, 500);
beep(a, 300);
beep(a, 150);
beep(aH, 500);
beep(gSH, 325);
beep(gH, 175);
beep(fSH, 125);
beep(fH, 125);
beep(fSH, 250);

delay(325);

beep(aS, 250);

Compte rendu TP - CE410

beep(dSH, 500);
beep(dH, 325);
beep(cSH, 175);
beep(cH, 125);
beep(b, 125);
beep(cH, 250);

delay(350);
}

void IMPERIALMARCH()
{

//Play first section
firstSection();

//Play second section
secondSection();

//Variant 1
beep(f, 250);
beep(gS, 500);
beep(f, 350);
beep(a, 125);
beep(cH, 500);
beep(a, 375);
beep(cH, 125);
beep(eH, 650);

delay(500);

//Repeat second section
secondSection();

//Variant 2
beep(f, 250);
beep(gS, 500);
beep(f, 375);
beep(cH, 125);
beep(a, 500);

Compte rendu TP - CE410

beep(f, 375);
beep(cH, 125);
beep(a, 650);

delay(650);
}

Compte rendu TP - CE410

## 9 Appendix C - Code appel des urgences

import tkinter as tk

import serial
from PIL import Image, ImageTk

# Set up serial communication

interface = "rfcomm0"
ser = serial.Serial(f"/dev/{interface}", 9600, timeout=1)

# Initialize Tkinter window

root = tk.Tk()
root.title("Serial Image Display")

# Load images once and store in a dictionary image_paths = {

"idle": "Images/walking.jpg",
"waiting": "Images/Blog-Image-Are-You-Ok.jpg", "ok": "Images/its_ok.png",
"danger": "Images/RAZ_Emeregency_Service.png", }

images = {
key: ImageTk.PhotoImage(Image.open(path)) for key, path in image_paths.items() }

# Create a label to display images

image_label = tk.Label(root) image_label.pack()

# Function to update the displayed image def update_image(status):

if status in images:
image_label.config(image=images[status])
image_label.image = images[status] # Keep reference to avoid garbage collection else:
print(f"Unknown status: {status}")

Compte rendu TP - CE410

# Main loop to read from the serial port and update the GUI def read_serial():

if ser.in_waiting > 0:
line = ser.readline().decode("utf-8").strip() update_image(line) # Update image based on received status root.after(100, read_serial) # Schedule next read

# Start reading serial data

root.after(100, read_serial)

# Run the Tkinter event loop try:

root.mainloop()
except KeyboardInterrupt:
print("Exiting program.")
ser.close()

Compte rendu TP - CE410

## 10 Appendix D - Code Matlab pour la caractérisation des paramètres

%% ========== ESTIMATION DES PARAMETRE DE L'ADXL 345 ========== close all;
DataX = readmatrix("AxeX345.txt_formate.txt");
DataY = readmatrix("AxeY345.txt_formate.txt");
DataZ = readmatrix("AxeZ345.txt_formate.txt");

%% ========== Offsets ==========
% === Calcul de l'offset sur X
dataY_x = DataY(:, 1); dataZ_x = DataZ(:,1);
rawX_offset = [dataY_x; dataZ_x]; tracerLoiNormaleHistogram(rawX_offset, 12, "0g offset axe X, ADXL345"); x_offset = mean(rawX_offset)

% === Calcul de l'offset sur Y
rawY_offset = [DataX(:,2); DataZ(:,2)]; tracerLoiNormaleHistogram(rawY_offset, 12, "0g offset axe Y, ADXL345"); y_offset = mean(rawY_offset)

% === Calcul de l'offset sur Z
rawZ_offset = [DataX(:,3); DataY(:,3)]; tracerLoiNormaleHistogram(rawZ_offset, 12, "0g offset axe Z, ADXL345"); z_offset = mean(rawZ_offset)

% ====== ADXL345
% x_offset = | -0.8703
% y_offset = | 0.8459
% z_offset = | 0.8846

% ====== ADXL359
% x_offset = 165.5092
% y_offset = 69.0781
% z_offset = -316.8318

Compte rendu TP - CE410

%% ========== Gains ========== raw_x1 = mean(DataX(:,1)); raw_y1 = mean(DataX(:,2)); raw_z1 = mean(DataX(:,3)); raw_x2 = mean(DataY(:,1)); raw_y2 = mean(DataY(:,2)); raw_z2 = mean(DataY(:,3)); raw_x3 = mean(DataZ(:,1)); raw_y3 = mean(DataZ(:,2));
raw_z3 = mean(DataZ(:,3));

% Paramètres donnés pour résoudre l'équation % sqrt( (ax)²+(by)² + (cz²)) = 1
% sqrt (dx)² + (ey)² + (fz²)) = 1
% sqrt( (gx)² + (hy)² + (iz)²) = 1

a = raw_x1-x_offset; b = raw_y1-y_offset; c = raw_z1-z_offset; % Exemple de valeurs d = raw_x2-x_offset; e = raw_y2-y_offset; f = raw_z2-z_offset; % Exemple de valeurs g = raw_x3-x_offset; h = raw_y3-y_offset; i = raw_z3-z_offset; % Exemple de valeurs

% Définir les équations sous forme de fonctions anonymes
equations = @(vars) [
sqrt((a * vars(1))^2 + (b * vars(2))^2 + (c * vars(3))^2) - 1; sqrt((d * vars(1))^2 + (e * vars(2))^2 + (f * vars(3))^2) - 1; sqrt((g * vars(1))^2 + (h * vars(2))^2 + (i * vars(3))^2) - 1 ];

% Valeurs initiales pour [x, y, z]
initial_guess = [0.5, 0.5, 0.5];

% Résolution avec fsolve
solution = fsolve(equations, initial_guess);

% Résultat
x = solution(1);
y = solution(2);
z = solution(3);

% Afficher la solution
disp(['Solution trouvée : x = ', num2str(x), ', y = ', num2str(y), ', z = ', num2str(z)]);

Compte rendu TP - CE410

% ====== ADXL345
% Solution trouvée : x = 0.0040005, y = 0.0039862, z = 0.0038718 % ====== ADXL359
% Solution trouvée : x = 3.9673e-05, y = 3.6318e-05, z = 4.0804e-05

%% Functions

function tracerLoiNormaleHistogram(data, nbHistogram, titre) % Calculer les paramètres de la loi normale
mu = mean(data); | % Moyenne des données
sigma = std(data); | % Ecart-type des données

% Créer l'histogramme des données
figure;
histogram(data, nbHistogram, 'Normalization', 'pdf'); | % Normalisation en PDF
hold on; | % Maintenir l'histogramme pour superposer la loi normale

% Tracer la courbe de la loi normale manuellement
x = linspace(min(data), max(data), 1000); | % Créer des points pour l'axe X
y = (1 / (sigma * sqrt(2 * pi))) * exp(-0.5 * ((x - mu) / sigma).^2); | % Densité de la loi normale
plot(x, y, 'r', 'LineWidth', 2); | % Tracer la loi normale (en rouge)

% Ajouter des labels et un titre
title(titre);
xlabel('Valeur (en g +- 20g)'); ylabel('Densité');
legend('Histogramme des données', 'Loi normale'); hold off; % Fin du maintien de la figure

end

Compte rendu TP - CE410

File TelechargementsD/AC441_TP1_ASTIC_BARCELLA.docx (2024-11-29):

# TP 1 : Identification de systèmes

ASTIC Hugo & BARCELLA Léo

18/10/2024

## Introduction

Le but de ce TP est de mettre en pratique les méthodes d'identifications vues en cours d'AC441 : ARX et ARMAX. Et aussi de voir l'effet de leurs différents paramètres.

% Définition des constantes

Ts = 1; % [s]

N = 50;

varBruit = 0;

### Définition du système

Nous allons utiliser la fonction idpoly. Cette fonction calcule la fonction de transfert du système à temps discret dépendant des polynomes A, B, C, D, F.

# 1. Méthodes d’estimation non paramétriques

## 1.1 Etude de l’influence du nombre d’échantillons de mesure

% Définition des polynomes de notre système

A = [1, -1.5, 0.7];

B = [0, 1, 0.5];

C = 1;

D = 1; F = 1;

sys = idpoly(A,B,C,D,F, varBruit, Ts);

href = impulse(sys, N);

% Définition de nos inputs

N_vector = [100, 500, 1000, 100000];

x = [0:1:50];

% Figure

figure;

plot(x, href, 'DisplayName', 'reference')

hold on;

error = zeros(length(N_vector),1);

for i=1:length(N_vector)

htest = estimateImpulse(N_vector(i), sys, Ts);

plot(x,htest, 'DisplayName', ['N = ' num2str(N_vector(i))]);

error(i) = mean(abs(href - htest));

end

title('Estimation du modèle avec CRA pour différentes valeurs de N');

xlabel("Temps [s]"); ylabel("Y");

legend show; % Afficher la légende

hold off; % Désactiver hold on si nécessaire

figure;

plot(N_vector, error);

title("Calcul de l'erreur moyenne");

xlabel("N"); ylabel("Erreur");

%plot(x, href, x, htest100, x, htest500, x, htest1000);

%legend("Reference", "N=100 points", "N=500 points", "N=1000 points")

Question 1 : Conclure quant à l’influence du paramètre N sur la précision du modèle obtenu.

On peut voir sur le graphique précédente que lorsque N augmente, la précision de notre estimation se rapproche de notre système.

Question 2 : Pourquoi un N grand permet-il d’avoir une meilleure modélisation ?

Prendre un N plus grand permet d'avoir plus de précision sur la sortie et d'avoir un signal riche en différentes informations (fréquences, pentes, allure des courbes...).

Question 3 : En pratique quel est l’inconvénient de prendre N très grand ?

Lorsque l'on prend un N très grand, le temps de l'étude du système devient aussi grand que N. Entrainant ainsi l'arrêt du système de production pendant toute la période de test. Il sera donc nécessaire de faire un compromis entre la durée du test et la précision du modèle.

## 1.2 Etude de l’influence de la variance du bruit

% Définition des polynomes de notre système

sigmaBruit = [0.1, 0.5, 1, 5, 10, 20, 30, 50];

N = 1000;

sys = idpoly(A,B,C,D,F, 0, Ts); % Sans bruit

href = impulse(sys, 50); % Réponse idéale

x = 0:1:50;

error = zeros(length(N_vector),1);

figure;

plot(href, 'DisplayName', 'reference');

hold on;

for i=1:length(sigmaBruit)

sys = idpoly(A,B,C,D,F, sigmaBruit(i), Ts);

htest = estimateImpulseNoise(N, sys, Ts);

plot(x,htest, 'DisplayName', ['N = ' num2str(sigmaBruit(i))]);

error(i) = mean(abs(href - htest));

end

legend show; % Afficher la légende

hold off; % Désactiver hold on si nécessaire

figure;

plot(sigmaBruit, error);

title("Calcul de l'erreur moyenne");

xlabel("Sigma carré"); ylabel("Erreur");

Question 1 : Conclure sur l'effet de sigma.

On voit sur le graphique précédent que lorsque sigma carré (la variance) augmente, l'erreur moyenne aussi.

Question 2 : Montrer l’influence de la variance sur les données obtenues avec la fonction SIM (on pourra également tracer la distribution gaussienne en fonction de la variance pour appuyer ses propos.

% Tracé des Gaussiennes

x = -5:0.01:5;

f1 = myGauss(x, 0, 1);

f2 = myGauss(x, 0, 2);

figure;

plot(x, f1, x, f2);

xlabel("x"); ylabel("f(x)");

title("Fonction gaussienne");

grid on;

legend("\sigma^2 = 1","\sigma^2 = 2");

D'après les résultats de la question 1, nous savons que lorsque la variance augmente, notre estimation s'écarte de notre modèle.

Cela s'explique par le fait que lorsque la variance augmente, le bruit est de plus en plus écarté de la valeur moyenne (moins centré autour de celle-ci), ce qui viens rajouter des erreurs lors de notre estimation.

# 2 - Méthode d'estimation paramétrique

## 2.1 - Etude de la méthode ARX

Question 1 : Tester l’influence du choix de la structure du modèle (degré du numérateur, degré du dénominateur, retard), et l’influence de la variance du bruit sur le résultat.

%% Définition des polynomes de notre système

A = [1, -1.5, 0.7];

B = [0, 1, 0.5];

C = 1;

D = 1; F = 1;

%Modèle ARX sans bruit

myfit = zeros(10);

for a=1:10

for b=1:10

sys = idpoly(A,B,C,D,F,0,Ts);

u = idinput(N, 'rbs');

y = sim(sys, u);

data = iddata(y,u,Ts);

htest = arx(data, [a,b,1]);

[ymod,fit,ic] = compare(data,htest);

myfit(a,b) = fit;

end

end

figure;

heatmap(myfit)

title("Taux de correspondance entre le modèle et l'estimation avec ARX");

xlabel("Degré du dénominateur (A)");

ylabel("Degré du numérateur (B)");

En lisant directement sur la Heatmap, on observe que la correspondance entre le modèle et l'estimation par la méthode ARX, est très élevée (100 %) pour des degrés de numérateur et de dénominateur supérieurs à 2. Ainsi pour minimiser le temps de calcul, nous pouvons prendre comme degré de numérateur et dénominateur : (na, nb) = (2, 2).

%% Modèle ARX avec bruit

varnoise=[0:0.02:2];

var_noise = zeros(1, length(varnoise));

for i=1:length(varnoise)

sys = idpoly(A,B,C,D,F,varnoise(i),Ts);

u = idinput(N, 'rbs');

y = sim(sys, u);

data = iddata(y,u,Ts);

htest_bruit = arx(data, [2,2,1]);

[ymod,fit,ic] = compare(data,htest_bruit);

var_noise(a) = fit;

end

figure;

plot(varnoise,var_noise);

title("Correspondance entre le modèle et l'estimation du modèle avec le bruit");

xlabel("Variance du bruit (sigma carré)");

ylabel("Correspondance [%]")

La correspondance entre le modèle et l'estimation ARX est maximale pour une variance du bruit de 0.18.

Question 2 : Analyser la valeur des paramètres identifiés ainsi que leur incertitude.

sys = idpoly(A,B,C,D,F,0.18,Ts);

u = idinput(N, 'rbs');

y = sim(sys, u);

data = iddata(y,u,Ts);

htest_opti = arx(data, [2,2,1]); % Correspondance à 100 %

htest_moins = arx(data, [1,5,1]); % Correspondance à 97.15 %

[A1,B1,C1,D1,F1,dA1,dB1,dC1,dD1,dF1]=polydata(htest_opti);

[A2,B2,C2,D2,F2,dA2,dB2,dC2,dD2,dF2]=polydata(htest_moins);

fprintf("Incertitude moyenne sur les coefficients de htest_opti %e\n",mean(abs([dA1, dB1])));

fprintf("Incertitude moyenne sur les coefficients de htest_moins %e\n",mean(abs([dA2, dB2])));

sd = 2; % Standard deviation

niq = nyquistplot(htest_opti, htest_moins);

showConfidence(niq, sd);

title("Diagramme de Nyquist des estimations, avec incertitudes");

xlabel("Axe des Réels"); ylabel("Axe des Imaginaires");

legend("Estimation 1, correspondance à 100 %", "Estimation 1, correspondance à 97 %");

On remarque que pour deux essais avec un ayant une meilleure correspondance que l’autre, les coefficients établis sont bien meilleurs et plus précis. On observe aussi bien moins d’incertitudes sur le diagramme de Nyquist.

## 2.2 Comparaison des méthodes ARX et ARMAX

Question 1, 2 et 3 : Analyser les résultats avec la méthodes des moindres carrés simples. Analyser aussi avec les différentes méthodes (ARX et ARMAX). Expliquez l'avantage d'une des méthodes par rapport aux autres.

%% Définition des polynomes de notre système

A = [1, -1.5, 0.7];

B = [0, 1, 0.5];

C = [1, -1.3, 0.9];

D = 1; F = 1;

variance = 0.1;

sys = idpoly(A,B,C,D,F,variance, Ts);

u = idinput(N, 'rbs');

y = sim(sys, u);

data = iddata(y,u,Ts);

heatmapCoeff(sys, data, 10); % Trace la heatmat de correspondace

% On trouve que le jeu 2,2 est très bien (100%).

htest = arx(data, [2,2,1]);

figure;

heatmapCoeffArmax(sys, data, 5, 2)

title("Correspondance avec ARMAX pour nc = 2")

figure;

heatmapCoeffArmax(sys, data, 5, 3)

title("Correspondance avec ARMAX pour nc = 3")

estimARMAX = armax(data, [2,1,2,1]);

estimARX=arx(data, [2,1,1]);

figure;

compare(data,estimARX,estimARMAX);

Après avoir sélectionné les meilleurs coefficients pour les essais avec ARX et ARMAX nous avons utilisé la fonction compare pour savoir quel modèle d’essai était le meilleur. Nous avons pu remarquer une meilleure correspondance pour le modèle ARMAX: cela est dû au fait que les erreurs de prédiction sont mises à jour à chaque itération dans cette méthode. La méthode ARX est plus utilisé s’il y a simplement un bruit blanc gaussien sans polynôme.

## Conclusion

Ce TP nous a permis d'améliorer nos connaissance sur le cours ainsi que d'avoir pu mettre en pratique les méthodes vues en cours. Nous avons aussi pu modifier les paramètres de celles-ci et voir leur effet.

function htest = estimateImpulse(N, sys, Ts)

% Définition de nos input

u = idinput(N, 'rbs');

y = sim(sys, u);

data = iddata(y,u,Ts);

htest = cra(data, 50, 10, 0);

end

function htest = estimateImpulseNoise(N, sys, Ts)

% Définition de nos input

u = idinput(N, 'rbs');

y = sim(sys, u, 'Noise');

data = iddata(y,u,Ts);

htest = cra(data, 50, 10, 0);

end

function f = myGauss(x, mu, sigma2)

f = (1 / sqrt(2 * pi * sigma2)) * exp(-((x - mu).^2) / (2 * sigma2));

end

function heatmapCoeff(sys, data, n_max)

%Modèle ARX sans bruit

myfit = zeros(n_max);

for a=1:n_max

for b=1:n_max

htest = arx(data, [a,b,1]);

[ymod,fit,ic] = compare(data,htest);

myfit(a,b) = fit;

end

end

figure;

heatmap(myfit)

title("Taux de correspondance entre le modèle et l'estimation avec ARX");

xlabel("Degré du dénominateur (A)");

ylabel("Degré du numérateur (B)");

end

function heatmapCoeffArmax(sys, data, n_max, c)

%Modèle ARX sans bruit

myfit = zeros(n_max);

for a=1:n_max

for b=1:n_max

htest = armax(data, [a,b,c,1]);

[ymod,fit,ic] = compare(data,htest);

myfit(a,b) = fit;

end

end

figure;

heatmap(myfit)

title("Taux de correspondance entre le modèle et l'estimation avec ARX");

xlabel("Degré du dénominateur (A)");

ylabel("Degré du numérateur (B)");

end

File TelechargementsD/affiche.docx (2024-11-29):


Jeudi 10 octobre, 20h-22h30

Entrée à 7€, crêpes et boissons à volonté.

Location patins incluse.


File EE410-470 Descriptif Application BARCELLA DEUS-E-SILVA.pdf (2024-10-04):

Projet EE410-EE470

# Capteur de chute, accéléromètre 3 axes

## Application du capteur

Nous allons utiliser un accéléromètre 3 axes, compatible Groove et basé sur un ADXL345. L’accéléromètre communique via le protocole I2C, et possède une librairie permettant de l’utiliser facilement sur Arduino. Nous allons utiliser le capteur pour réaliser un capteur de chute. L’objectif de celui-ci est de détecter si une chute a été faite par la personne portant le capteur.
Si nous détectons une chute, l’utilisateur sera averti par un vibreur. Il disposera alors d’un délai de 10 secondes pour confirmer qu’il n’est pas inconscient par l’intermédiaire d’un bouton poussoir. S’il appuie sur le bouton pendant ce délai, l’alerte sera annulée. S’il ne fait rien pendant 10 secondes, dans ce cas, nous sommes en présence d’une chute réelle.

## Déroulement des tests

Voici les tests que nous allons réaliser :
- Test statique, nous mesurons l’accélération sur le capteur lorsqu’il est posé et qu’il ne bouge pas
- Test en marchant :
- Simulation de marche : nous allons faire avancer le capteur à différentes allures sur un plan à allure constante.
Mise en pratique : un fil est enroulé autour d’un moteur qui tourne à vitesse constante et le capteur est attaché au bout. (simulation vitesse constante).
- Test en conditions réelles : on met le capteur sur une personne qui marche à une allure normale. Ce test permet de vérifier la simulation de marche.
- Test de chute :
- Simulation de chute droite : Nous allons mesurer l’accélération lorsque le capteur tombe vers le sol.
Mise en pratique : le capteur est attaché à un fil et un poid, l’autre extrémité du fil est fixée. On pousse l’ensemble poids-capteur, qui tombe et qui est retenu à la fin par le fil.
- Simulation de chute en avant : Nous allons mesurer l’accélération lorsque le capteur tombe en avant avec une base au sol fixe.
Mise en pratique : le capteur est attaché au sommet d’un bâton en bois, la base du bâton est fixée au sol. On pousse légèrement le capteur pour engendrer la chute. On détectera une chute en avant de manière circulaire.
- Test en conditions réelles, chute droite : On met le capteur sur une personne qui s’effondre au sol sur un matelas.
- Test en conditions réelles, chute en : On met le capteur sur une personne qui chute en avant sur un matelas.

Les “Simulations” sont des versions des tests en conditions réelles mais que nous pouvons reproduire et obtenir des résultats constants. Les “Tests en conditions réelles” vont nous permettre de vérifier si nos “simulations” sont assez proches de la réalité. Nous allons ainsi d’ajuster nos paramètres de test pour se rapprocher au mieux de la réalité.
Nous allons aussi utiliser les lois de la physique pour vérifier si les résultats que nous obtenons sont cohérents.

Le but de ces tests est de nous permettre d’identifier nos 3 cas clés : Statique, Marche et Chute.

Léo BARCELLA
José De Deus E Silva




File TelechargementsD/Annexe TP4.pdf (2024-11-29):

# Annexes


Annexe 1 : Relevé des signaux

Annexe 2 : Caractéristique XY

Annexe 3 : Relevé de la distorsion de croisement

## Test de la maquette


Annexe 4 : Visualisation du courant Ic

+ à 10 Hz

Annexe 5 : Visualisation du courant Ic

+ à 1 kHz

Annexe 6 : Mesure de la tension de seuil sans aucune compensation


Annexe 7 : Mesure de la tension de seuil avec compensation par diodes

Annexe 8 : Mesure de la tension de seuil avec compensation par AOP à 1 kHz


Annexe 9 : Mesure de la tension de seuil avec compensation par AOP à 20 kHz

Annexe 10 : Visualisation de la distorsion de croisement avec compensation par AOP à 1 kHz


Annexe 11 : Mesure de bande passante à -3 dB

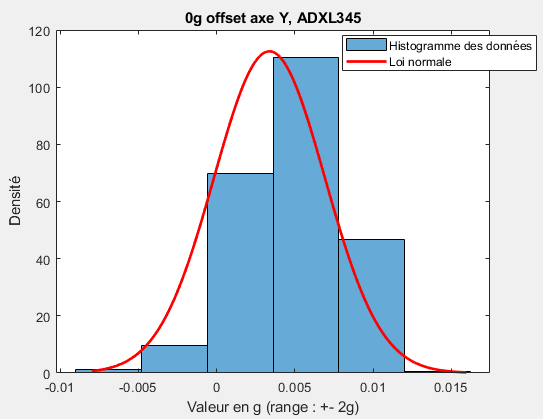
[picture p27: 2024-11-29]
PartieMatlab/Images/ADXL345_0g_offset_Y.png

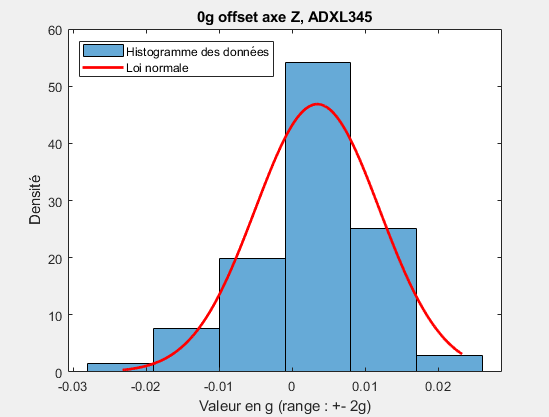
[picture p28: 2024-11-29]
PartieMatlab/Images/ADXL345_0g_offset_Z.png

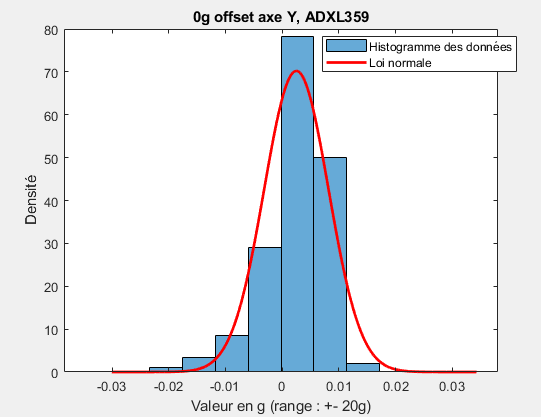
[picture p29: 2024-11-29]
PartieMatlab/Images/ADXL359_0g_offset_Y.png

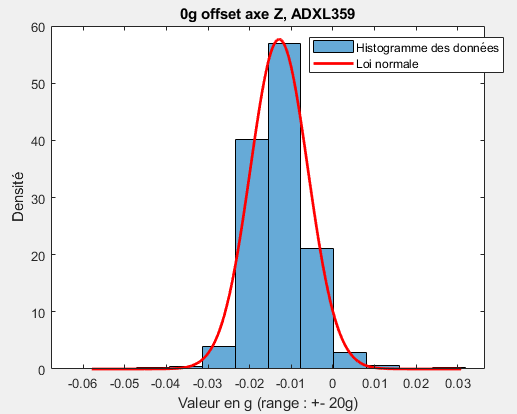
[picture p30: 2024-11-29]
PartieMatlab/Images/ADXL359_0g_offset_Z.png

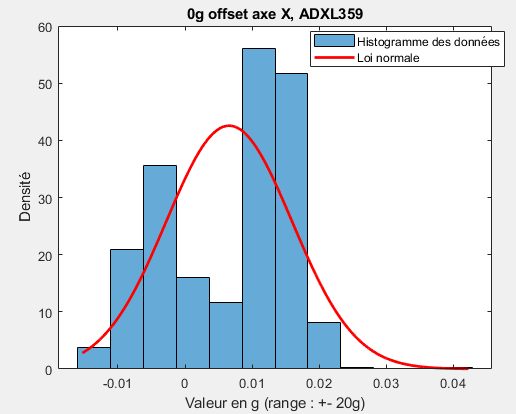
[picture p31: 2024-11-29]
PartieMatlab/Images/ADXL359_0g_offset_X.png

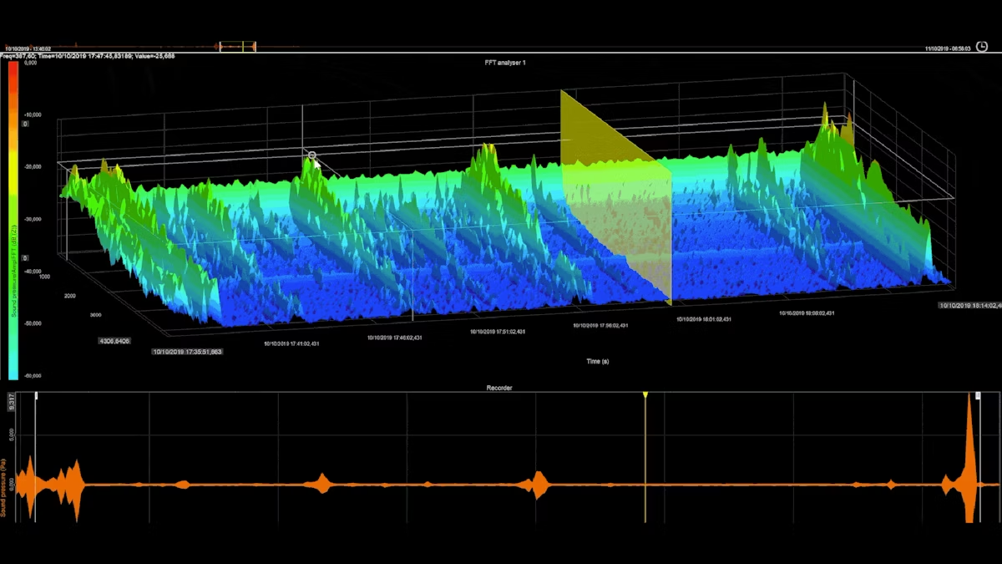
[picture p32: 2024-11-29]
TelechargementsD/1667847679-dewesoft-x-3d-graph-optimized.png

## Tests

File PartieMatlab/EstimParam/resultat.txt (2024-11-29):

547,767,25014,25031.74
509,621,24969,24981.91
574,614,24842,24856.22
544,668,24820,24834.95
559,636,24860,24874.42
502,564,24803,24814.49
492,661,24821,24834.67
524,704,24963,24978.42
423,666,24838,24850.53
700,618,24883,24900.52
580,727,24847,24864.4
507,781,24771,24788.5
714,741,25031,25052.14
586,571,24825,24838.48
430,774,24921,24936.73
399,762,24996,25010.8
736,790,24836,24859.46
579,786,24941,24960.1
593,634,24803,24818.19
568,640,24850,24864.73
549,791,24775,24793.7
605,752,24932,24950.67
709,727,24855,24875.74
646,671,24846,24863.45
612,781,24941,24960.73
470,666,24756,24769.42
427,682,24876,24889.01
700,678,24919,24938.05
479,745,24797,24812.81
688,697,24933,24952.23
580,802,24979,24998.6
526,705,24882,24897.54
635,670,24814,24831.16
581,723,24909,24926.26
464,680,25044,25057.53
452,650,24968,24980.55
588,768,24879,24897.8
513,670,25065,25079.2
693,710,24858,24877.79
549,690,24864,24879.63
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

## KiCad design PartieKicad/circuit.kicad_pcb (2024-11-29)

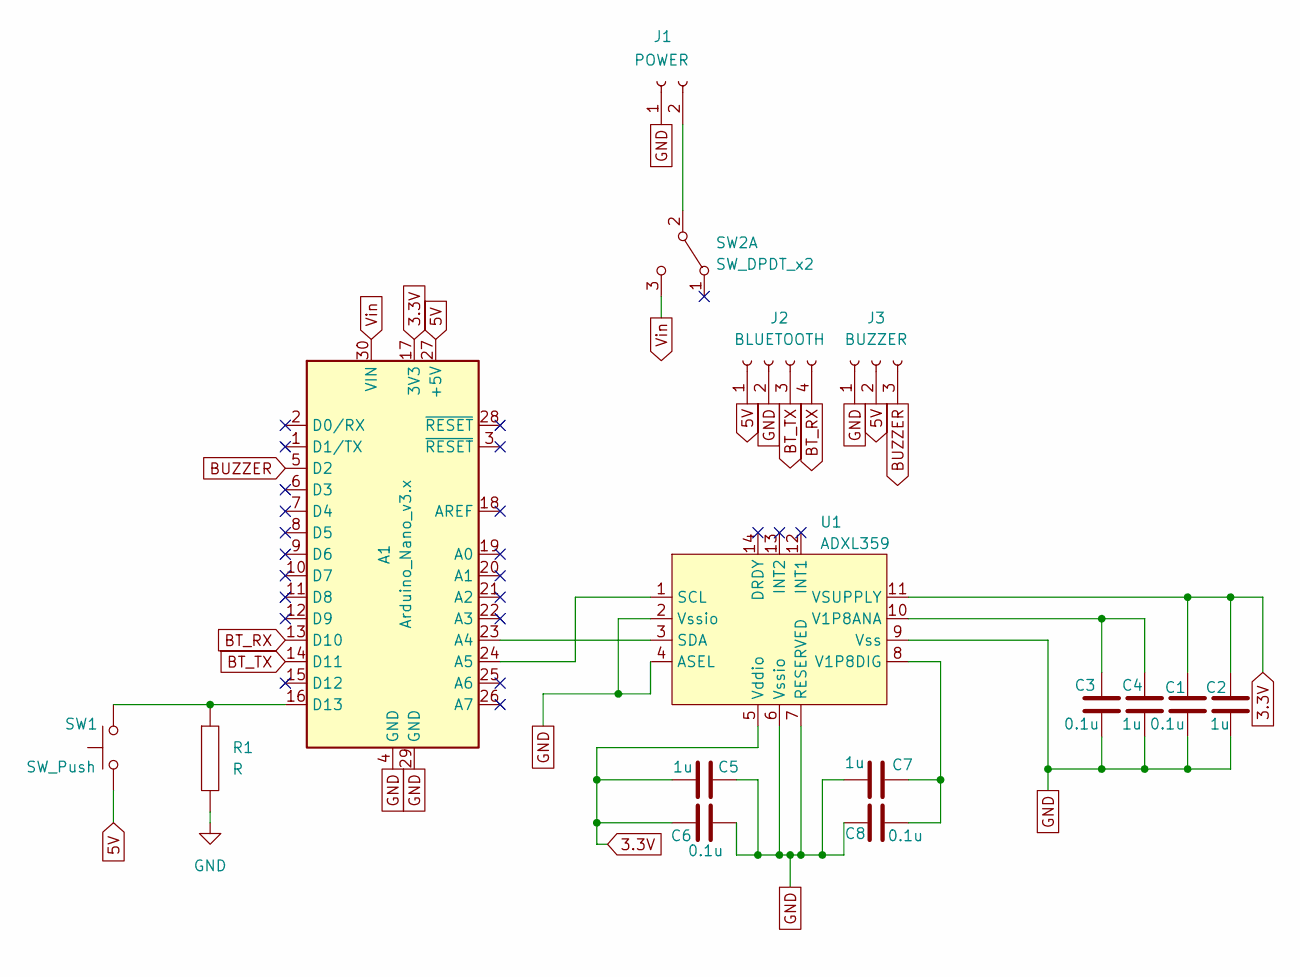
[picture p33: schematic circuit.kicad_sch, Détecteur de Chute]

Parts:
A1: Arduino_Nano_v3.x; Arduino_Nano
C1, C3, C6, C8: 0.1u; C_1206_3216Metric
C2, C4, C5, C7: 1u; C_1206_3216Metric
J1: POWER; PinHeader_1x02_P2.54mm_Vertical
J2: BLUETOOTH; PinHeader_1x04_P2.54mm_Vertical
J3: BUZZER; PinHeader_1x03_P2.54mm_Vertical
R1: R; R_1206_3216Metric_Pad1.30x1.75mm_HandSolder
SW1: SW_Push; sw_push_5mm
SW2: SW_DPDT_x2; PinHeader_1x03_P2.54mm_Vertical
U1: ADXL359

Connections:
3.3V: A1.17 (3V3), C1.1, C2.1, C5.2, C6.2, U1.5 (Vddio), U1.11 (VSUPPLY)
5V: A1.27 (+5V), J2.1, J3.2, SW1.1
BT_RX: A1.13 (D10), J2.4
BT_TX: A1.14 (D11), J2.3
BUZZER: A1.5 (D2), J3.3
GND: A1.4 (GND), A1.29 (GND), C1.2, C2.2, C3.2, C4.2, C5.1, C6.1, C7.2, C8.2, J1.1, J2.2, J3.1, R1.2, U1.2 (Vssio), U1.4 (ASEL), U1.6 (Vssio), U1.7 (RESERVED), U1.9 (Vss)
unnamed: A1.23 (A4), U1.3 (SDA)
unnamed: A1.24 (A5), U1.1 (SCL)
unnamed: A1.16 (D13), R1.1, SW1.2
unnamed: J1.2, SW2.2 (B)
unnamed: C3.1, C4.1, U1.10 (V1P8ANA)
unnamed: C7.1, C8.1, U1.8 (V1P8DIG)
Vin: A1.30 (VIN), SW2.3 (C)

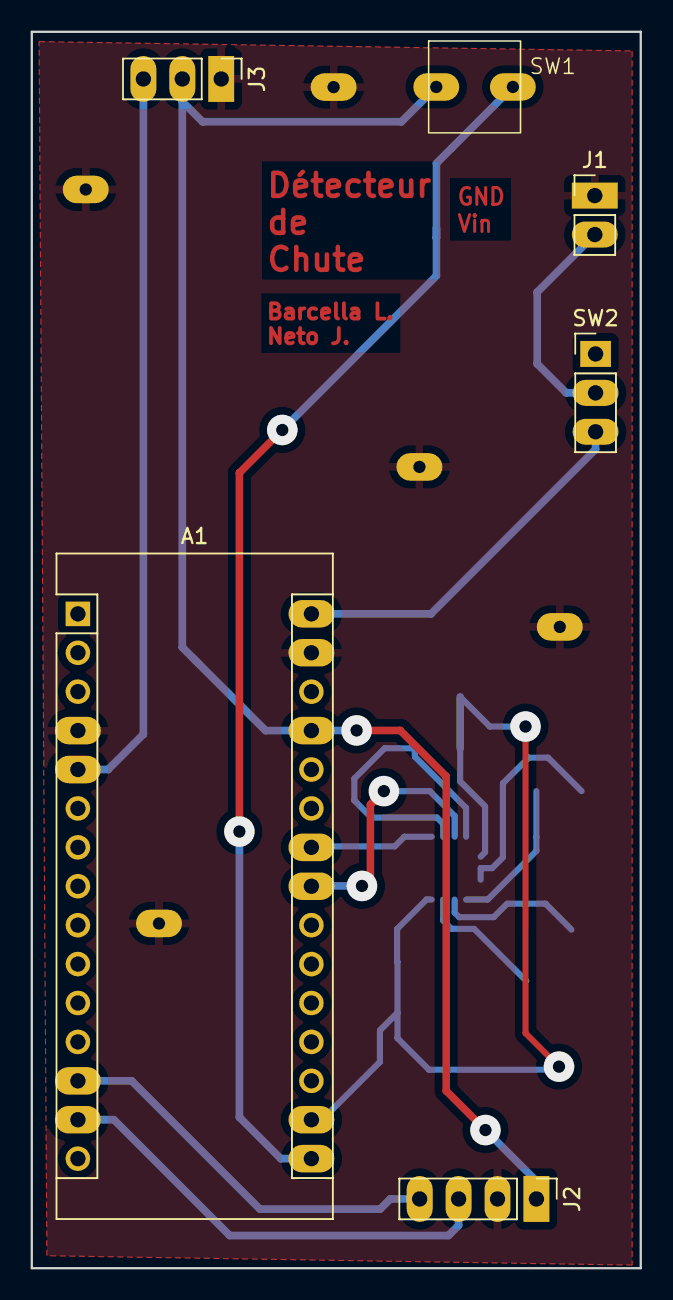
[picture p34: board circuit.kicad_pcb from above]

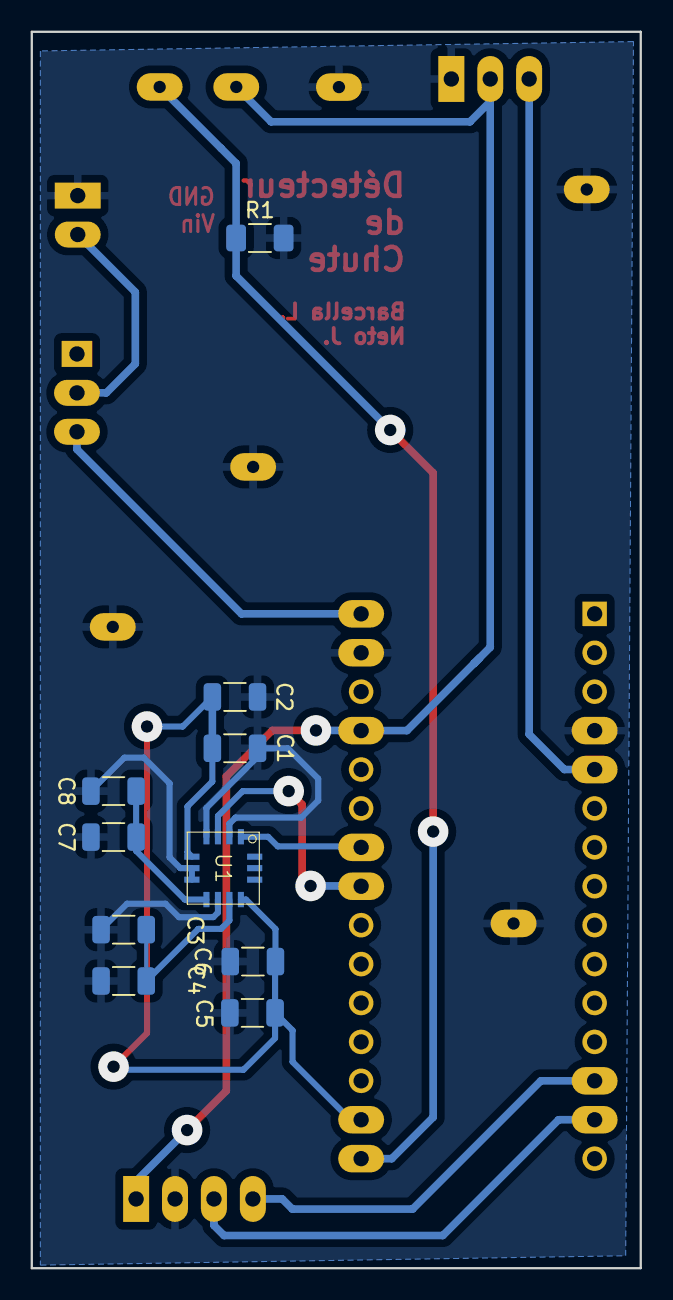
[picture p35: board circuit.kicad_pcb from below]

Board: 2 copper layers, 39.7 x 80.7 mm, 16 parts (10 on the bottom side), 13 nets.

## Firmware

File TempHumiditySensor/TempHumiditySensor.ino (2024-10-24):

// Example testing sketch for various DHT humidity/temperature sensors
// Written by ladyada, public domain

// REQUIRES the following Arduino libraries:
// - DHT Sensor Library: https://github.com/adafruit/DHT-sensor-library
// - Adafruit Unified Sensor Lib: https://github.com/adafruit/Adafruit_Sensor
#include <Arduino.h>
#include <TM1637Display.h>
#include <SoftwareSerial.h>

//Serial config for bluetooth module
SoftwareSerial mySerial(10, 11); // RX, TX

// Module connection pins (Digital Pins)
#define CLK 6
#define DIO 7

// The amount of time (in milliseconds) between tests
#define TEST_DELAY   2000

#include "DHT.h"
#include <Adafruit_Sensor.h>

#define DHTPIN 2     // Digital pin connected to the DHT sensor
// Feather HUZZAH ESP8266 note: use pins 3, 4, 5, 12, 13 or 14 --
// Pin 15 can work but DHT must be disconnected during program upload.

#define BUTTONPIN 3

// Uncomment whatever type you're using!
#define DHTTYPE DHT11   // DHT 11
//#define DHTTYPE DHT22   // DHT 22  (AM2302), AM2321
//#define DHTTYPE DHT21   // DHT 21 (AM2301)

// Connect pin 1 (on the left) of the sensor to +5V
// NOTE: If using a board with 3.3V logic like an Arduino Due connect pin 1
// to 3.3V instead of 5V!
// Connect pin 2 of the sensor to whatever your DHTPIN is
// Connect pin 3 (on the right) of the sensor to GROUND (if your sensor has 3 pins)
// Connect pin 4 (on the right) of the sensor to GROUND and leave the pin 3 EMPTY (if your sensor has 4 pins)
// Connect a 10K resistor from pin 2 (data) to pin 1 (power) of the sensor

// Initialize DHT sensor.
// Note that older versions of this library took an optional third parameter to
// tweak the timings for faster processors.  This parameter is no longer needed
// as the current DHT reading algorithm adjusts itself to work on faster procs.
DHT dht(DHTPIN, DHTTYPE);

float maxTemperature = 0;
TM1637Display display(CLK, DIO);
uint8_t blank[] = { 0x00, 0x00, 0x00, 0x00 };

void setup() {
  Serial.begin(9600);
  Serial.println(F("DHTxx test!"));
  pinMode(BUTTONPIN, INPUT);
  
  while (!Serial) {
    ; // wait for serial port to connect. Needed for native USB port only
  }

  mySerial.begin(9600);
  dht.begin();
}

void loop() {
  // Wait a few seconds between measurements.
  delay(2000);

  // Reading temperature or humidity takes about 250 milliseconds!
  // Sensor readings may also be up to 2 seconds 'old' (its a very slow sensor)
  float h = dht.readHumidity();
  // Read temperature as Celsius (the default)
  float t = dht.readTemperature();
  // Read temperature as Fahrenheit (isFahrenheit = true)
  float f = dht.readTemperature(true);

  if (t > maxTemperature) {
    maxTemperature = t;
  }

  // Check if any reads failed and exit early (to try again).
  if (isnan(h) || isnan(t) || isnan(f)) {
    Serial.println(F("Failed to read from DHT sensor!"));
    return;
  }

  // Compute heat index in Fahrenheit (the default)
  float hif = dht.computeHeatIndex(f, h);
  // Compute heat index in Celsius (isFahreheit = false)
  float hic = dht.computeHeatIndex(t, h, false);

    

  int buttonValue = digitalRead(BUTTONPIN);

  Serial.print("Button Value : ");
  Serial.println(buttonValue);

  if (buttonValue == 1) {
    display.setBrightness(0x0f);
    Serial.print("Max temperature = ");
    Serial.println(maxTemperature);
    int temp = maxTemperature;
    display.showNumberDec(temp, false);
  }
  else {
    display.setSegments(blank);
    Serial.print(F("Humidity: "));
    Serial.print(h);
    Serial.print(F("%  Temperature: "));
    Serial.print(t);
    Serial.print(F("°C "));
    Serial.print(f);
    Serial.print(F("°F  Heat index: "));
    Serial.print(hic);
    Serial.print(F("°C "));
    Serial.print(hif);
    Serial.println(F("°F"));
  }
}

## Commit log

2024-09-20 Example temperature sensor
2024-10-04 add analysis notebook and files to sensor schema
    [capture.csv, capture2.csv, circuit.kicad_pcb, circuit.kicad_sch]
2024-10-11 organize libraries
    [arduino_float_data.csv]
2024-10-14 Fall Detector Working (V1)
    Détection de chute qui marche quoi !
    En 3h j'ai fait l'éuivalent de 9h de projet...
    [Capture1.csv]
2024-10-14 Ajustement des valeurs fall detector + images
    [AnalyseCapture1.xlsx]
2024-10-24 code python working
    [arduino_float_data.csv]
2024-10-24 seance demo
    [arduino_float_data_v2.csv]
2024-11-17 pcb v1.1
    [circuit.kicad_pcb, circuit.kicad_sch]
2024-11-19 pcb v2.1
    [circuit.kicad_pcb, circuit.kicad_sch]
2024-11-20 Work PCB
    Small Fix on PCB
    + Solve error on the resistance for the button (pcb)
    [circuit.kicad_pcb, circuit.kicad_sch]
2024-11-22 Start Creation Library
    Je débugue la librairie déja donnée pour l'adxl345. Je décode et essaie de tout comprendre...
    Objectif : pouvoir le faire à la main pour plus tard
2024-11-29 Fin du projet
    [carte-ee410.kicad_pcb, carte-ee410.kicad_sch, circuit.kicad_pcb, circuit.kicad_sch]
2024-12-06 Cleaning + CR
    [arduino_float_data.csv, arduino_float_data_v2.csv, capture.csv, capture2.csv]
